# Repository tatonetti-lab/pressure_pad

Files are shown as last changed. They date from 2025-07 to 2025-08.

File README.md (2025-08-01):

# Pressure Sensor Pad for Real-Time Ulcer Detection
A smart pressure-sensing pad for early detection of pressure ulcers.

## 📖 Table of Contents
- [🔬 Project Overview](#-project-overview)
  - [Motivation](#motivation)
- [🛠 Hardware](#-hardware)
  - [Core Components](#core-components)
  - [Circuit Summary](#circuit-summary)
- [💻 Software \& Interface](#-software--interface)
  - [Arduino Firmware](#arduino-firmware)
  - [User Interface](#user-interface)
- [🧪 Testing \& Usage](#-testing--usage)
  - [Power Supply](#power-supply)
  - [Firmware Upload](#firmware-upload)
  - [Hardware Guide](#hardware-guide)
  - [Software Guide](#software-guide)
- [📊 Current Results](#-current-results)
- [⚠️ Current Limitations](#️-current-limitations)
- [🔮 Roadmap](#-roadmap)
- [👷 Troubleshooting Guide](#-troubleshooting-guide)
- [🧱 File Structure](#-file-structure)
- [✍️ Authors](#️-authors)

## 🔬 Project Overview
This project is a custom-built pressure sensor pad designed to detect and monitor pressure distribution in surgical and ICU settings. The goal is to identify high-risk regions for pressure ulcers in real time, aiding in preventative care for hospitalized patients.

### Motivation
Pressure ulcers are a major complication for bedridden or post-surgical patients. This device aims to reduce incidence by:
- Continuously monitoring pressure points beneath a patient
- Alerting clinicians to prolonged or high-risk pressure areas
- Improving quality of care, particularly in oncology and ICU units
>For a more in-depth analysis, go to [`/Docs/Pressure Pad Presentation.pdf`](https://github.com/tatonetti-lab/pressure_pad/blob/main/Docs/Pressure%20Pad%20Presentation.pdf)

## 🛠 Hardware

### Core Components
- **Microcontroller:** `Arduino GIGA R1 WiFi`
- **Sensor Matrix:** 23 x 32 grid using `Velostat` (a piezoresistive plastic that changes resistance under pressure)
- **Switching Logic:** `ADG728` I2C analog switches for matrix scanning
- **PCB:** Custom `KiCad` board with routed traces for all sensor inputs
- **Display:** `Arduino GIGA Display Shield` for on-device heatmap visualization

### Circuit Summary
- One row and one column are selected via ADG728s
- Voltage from each cell is read via the Arduino ADC
- Pressure intensity is inferred from voltage level
- Repeats rapidly across entire matrix to produce a live heatmap
>Circuit design allows scanning one row and one column at a time to measure pressure at each intersection.

## 💻 Software & Interface

### Arduino Firmware
- Collects analog pressure data from the sensor matrix
- Controls ADG728s via I2C to select matrix zones
- Sends data to GIGA Display for visualization

### User Interface
- Built in `SquareLine Studio`
- Features:
  - Home Screen
  - Live zone overview
  - Full pressure grid view
  - Future: historic trends + movement alerts

## 🧪 Testing & Usage

### Power Supply
- Power via USB-C or external 5V line

### Firmware Upload
1. Connect `Arduino GIGA R1 WiFi` via USB
2. Download the `PressurePadApp.zip`
3. Upload `PressurePadApp.ino` sketch using [**`Arduino IDE`**](https://www.arduino.cc/en/software/)

>Necessary libraries: `Arduino_GigaDisplayTouch`, `Arduino_GigaDisplay_GFX`, and `lvgl` **(v8.3.11)**.

### Hardware Guide
1. Insert the `Arduino GIGA Display Shield` into `Arduino GIGA R1`
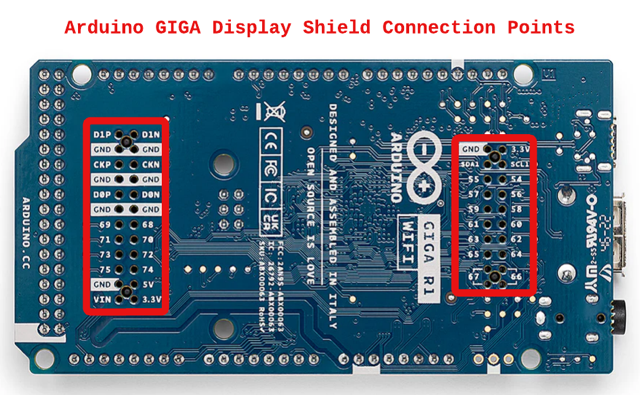
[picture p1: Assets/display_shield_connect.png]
display shield connect
   
2. Insert the `Arduino GIGA R1 WiFi + Display` into the PCB (female headers facing down)
   
3. Position the `pressure pad` so that the connection points are at the bottom right (`red` side facing up)
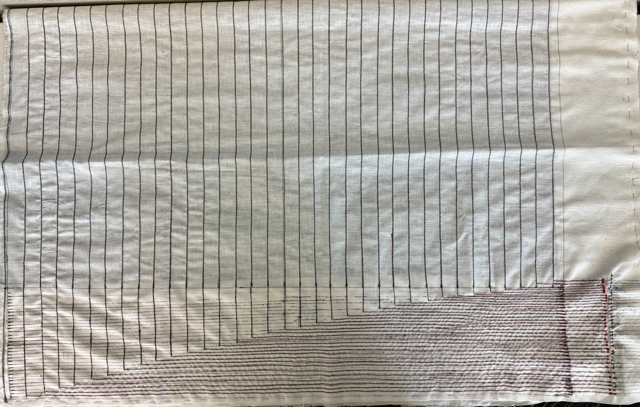
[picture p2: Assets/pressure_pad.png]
pressure pad
   
4. Wire pad to PCB:
   - **Red leads** → `DEMULTIPLEXER OUTPUTS` (vertical header, right)
   - **Blue leads** → `MULTIPLEXER INPUTS` (horizontal header, bottom)
5. Power the board

### Software Guide
>Once the system is powered on and the display shield is connected, the UI will launch automatically.

**Main Screens:**
- **`Home Page:`** Displays system status and navigation buttons to access `Live Data Overview` and `Historic Data` pages
- **`Live Data Overview:`** Displays 12 large, tappable buttons, each corresponding to a zone of the pressure pad
  - Each button changes color in real time based on average pressure in that region
  - Tap a button to enter that zone’s detailed heatmap
- **`Live Data:`** Shows an 8×8 heatmap of the selected zone from the pad
  - Color-coded for quick identification of high-pressure points
  - Updated continuously based on sensor readings
- **`Historic Data (Under Development):`** Will display trends in pressure over time and trigger alerts for high-risk zones

**Navigation:**
- Touchscreen is fully interactive (capacitive touch)
- Use on-screen buttons to switch between screens
- Tap return icons to go back to previous pages

**Interpreting the Heatmap:**
- Axis orientation matches the physical pad as connected to the PCB:
  - X-axis runs **right to left**
  - Y-axis runs **bottom to top**
- Colors represent pressure levels:
  - 🔴 Red = high pressure (risk of ulcers)
  - 🟣 Purple = moderate
  - 🔵 Blue = minimal or no pressure
- Live updates occur at ~20–50ms per cell

## 📊 Current Results
- All cells return live analog values
- Pressure heatmap successfully displayed in real time
- PCB assembled and functioning as intended
- Future test deployment planned at Cedars-Sinai surgical suite

## ⚠️ Current Limitations

- Top sensor row (y = 24) currently shows noise due to physical layout constraints
- Calibration may vary with sensor wear
- Data is real-time only; historic pressure history not yet stored
- No wireless/cloud connectivity yet
- Must be handled carefully to avoid flex damage in Velostat

## 🔮 Roadmap

| Milestone                     | Status     |
|------------------------------|------------|
| Initial prototype            | ✅ Complete |
| PCB design and assembly      | ✅ Complete |
| Real-time display            | ✅ Complete |
| Historic data + alert logic  | 🔄 In progress |
| Clinical suite testing       | 🔜 Planned |

## 👷 Troubleshooting Guide

| Problem                                      | Possible Cause                                             | Solution                                                                 |
|----------------------------------------------|------------------------------------------------------------|--------------------------------------------------------------------------|
| Heatmap shows no data                        | Arduino not powered or not connected properly              | Check USB/5V supply and USB cable connection                            |
| Only partial pad is active                   | Incorrect multiplexer/demultiplexer wiring                 | Verify wiring between PCB and pad (red = demux, blue = mux)             |
| Data appears inverted or mirrored            | Pad is oriented incorrectly                                | Rotate the pad so the connection points are at the bottom right         |
| Zones not updating in UI                     | I2C communication issue or faulty ADG728                   | Check I2C addresses and power to switches                               |
| Arduino not recognized in IDE                | Wrong port or missing driver                               | Ensure correct port is selected and install board package in Arduino IDE |
| No image shown on display                    | Display shield not connected correctly                     | Reseat the display shield onto Arduino GIGA pins                        |
| Colors frozen on screen                      | Loop not running or memory issue                           | Reset Arduino, monitor serial for errors                                |
| Boot0 light flashing red after upload        | Invalid code upload or memory overflow                     | Double-click the RST button on top right of the Arduino (back-side) & reupload code |
| Solder joints not connecting (Arduino back)  | No through-holes to allow solder to bridge to PCB          | Use angled headers, conductive epoxy, or jumper wires to reroute traces |

## 🧱 File Structure
<pre>
pressure_pad/
├── PressurePadApp/             # Arduino firmware and UI code
│   ├── PressurePadApp.ino
│   ├── ui_*.c / .h             # UI pages and assets
│   └── CMakeLists.txt
├── KiCad/                      # PCB schematic and layout files
│   └── pressure_pad.kicad_*
├── Assets/                     # Images for documentation
│   └── *.png
├── Docs/                       # Slides, references, design notes
│   └── *.pdf
├── DenoisingAutoencoder_OLD/   # Legacy Python scripts and ML notebooks
│   ├── no_touch_set/
│   ├── 6x6/
│   ├── *.ipynb
│   └── pressure_pad_study.db
└── .vscode/                    # VSCode config (not necessary for implementation)
</pre>

## ✍️ Authors

- [@AlexAhitov](https://github.com/AlexAhitov)

[**Back to the top**](#pressure-sensor-pad-for-real-time-ulcer-detection)

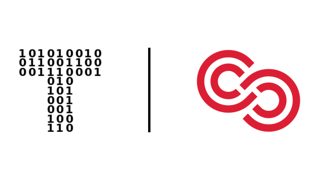
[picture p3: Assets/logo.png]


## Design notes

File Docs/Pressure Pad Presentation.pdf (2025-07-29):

# Real-Time Pressure Sensor

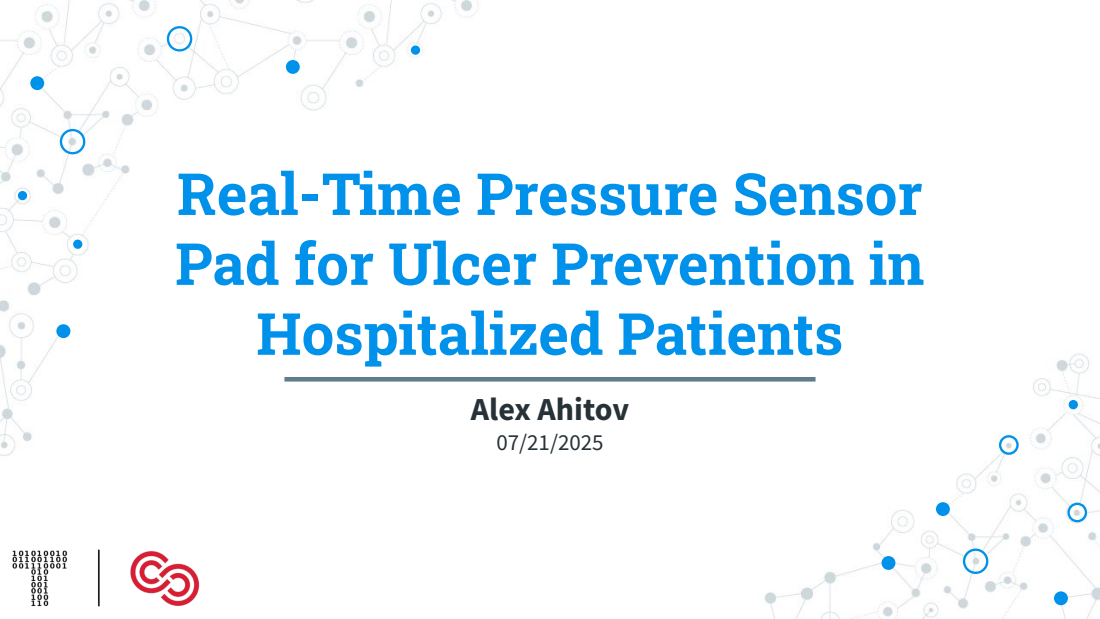
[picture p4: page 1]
Alex Ahitov

Pad for Ulcer Prevention in
Hospitalized Patients

### Motivation / Aim

Clinical Problem:
◎ Ulcers and bedsores are common in ICU & surgical patients. Impact:
◎ Increase infections, hospital stays, and costs.
Project Aim:
◎ Real-time pressure monitoring to prevent ulcers by guiding

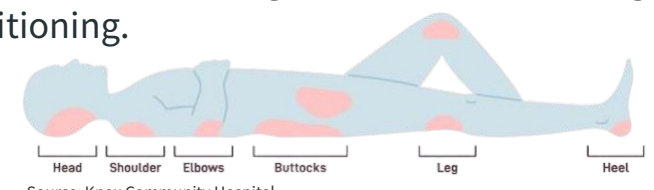
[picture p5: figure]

timely repositioning.

Source: Knox Community Hospital (https://www.kch.org/pressure-ulcers) | 2

### Background

Current Standard of Care
◎ Manual turning schedules or subjective monitoring.
Limitations:
◎ No continuous, objective feedback for nurses or physicians.
Our Approach:
◎ A real-time pad that provides actionable data to healthcare professionals.

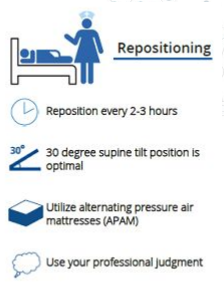
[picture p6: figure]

3

Source: Wound Care Surgeons (https://www.woundcaresurgeons.org/blogs/all-you-need-to-know-about-pressure-ulcers)

### Methods: System Development Overview

◎ Pipeline:

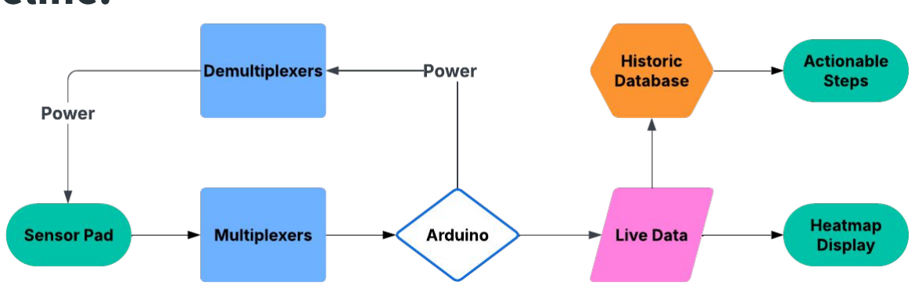
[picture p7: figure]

◎ Key Design Goals: High resolution, low noise, scalable to full-body pad.

4

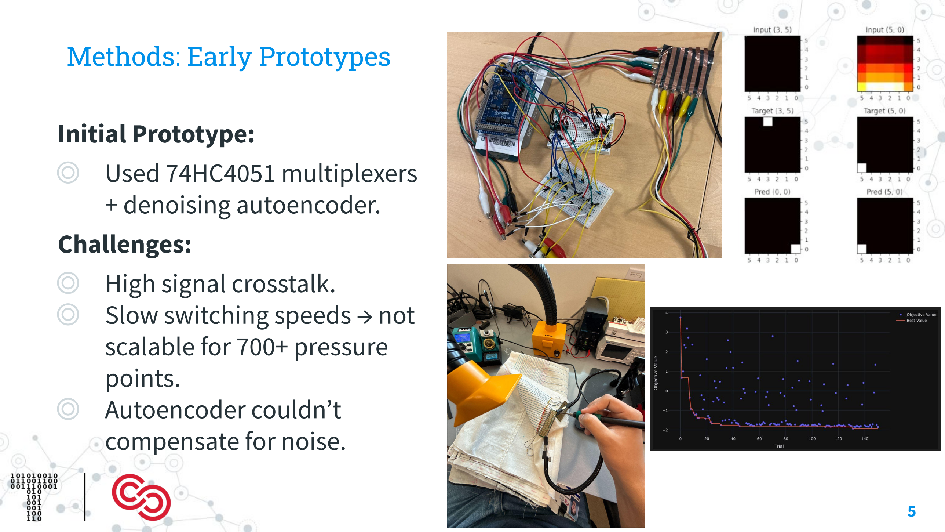
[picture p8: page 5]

### Methods: Early Prototypes

Initial Prototype: ◎ Used 74HC4051 multiplexers

+ denoising autoencoder.
Challenges: ◎ High signal crosstalk. ◎ Slow switching speeds → not

scalable for 700+ pressure points.
◎ Autoencoder couldnʼt
compensate for noise.

5

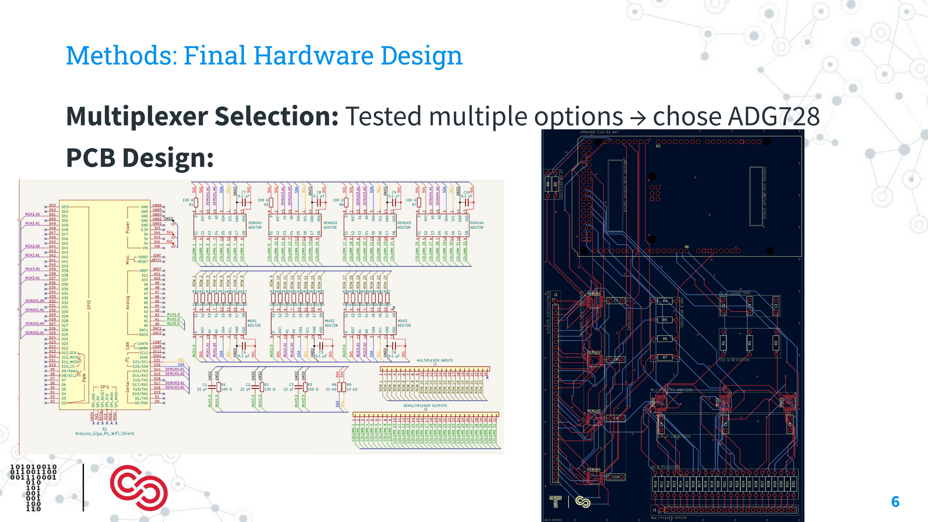
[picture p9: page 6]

### Methods: Final Hardware Design

Multiplexer Selection: Tested multiple options → chose ADG728 PCB Design:

6

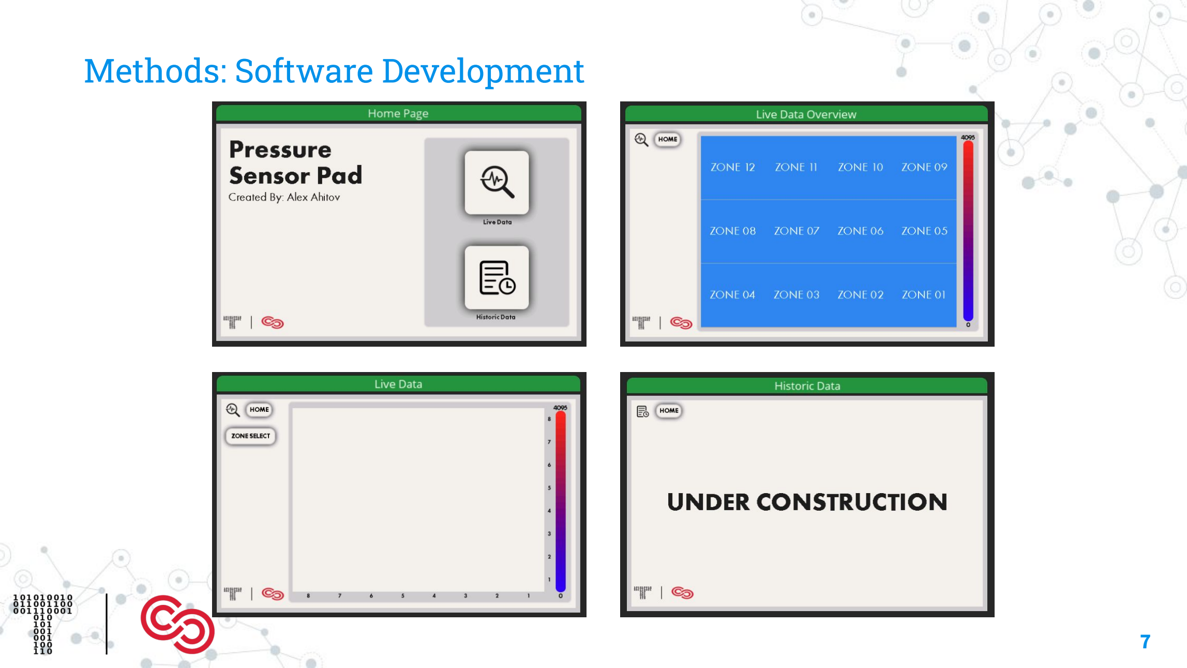
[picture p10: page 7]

### Methods: Software Development

7

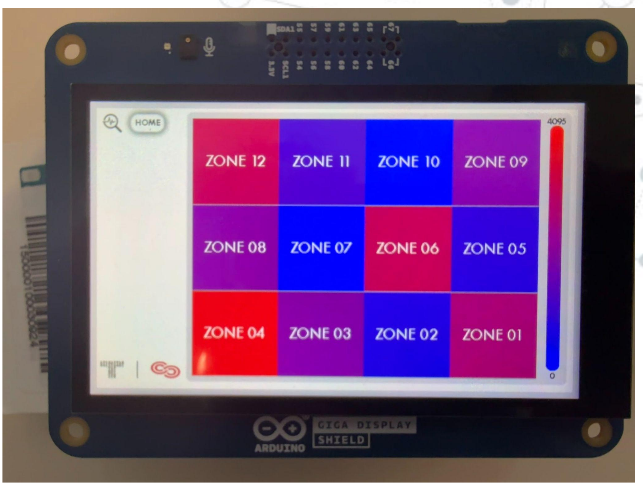
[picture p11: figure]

### Current Results

What Works Now: ◎ Real-time data

visualization for all zones. ◎ Zone recoloring reflects relative pressure risk.
Current Status: ◎ PCB boards arriving today

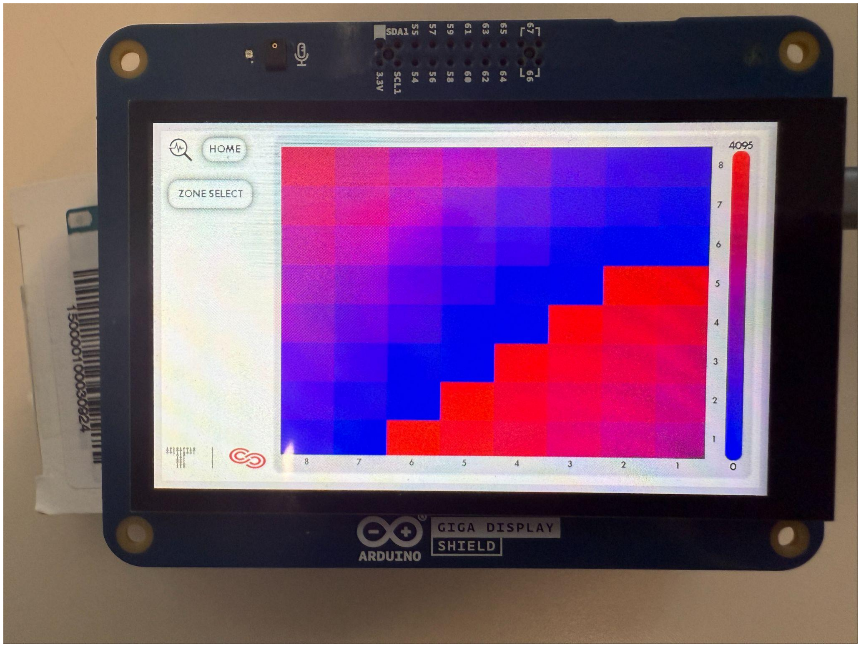
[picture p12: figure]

→ no live demo yet.

8

### Future Steps

Software:
◎ Add historic data logging to show how long high
pressure persists.
Clinical Testing:
◎ Test out pressure pad in a Cedars-Sinai surgical
suite.

9

Big Vision:
◎ Automated repositioning
alerts for nurses → reduce ulcer incidence.

### Conclusion

✓ Built a working real-time pressure-sensing pad with live heatmap visualization.
✓ Hardware and software ready for clinical testing; PCB arriving today.
✓ Potential to reduce ulcer incidence by providing actionable repositioning data for ICU and surgical patients.

10

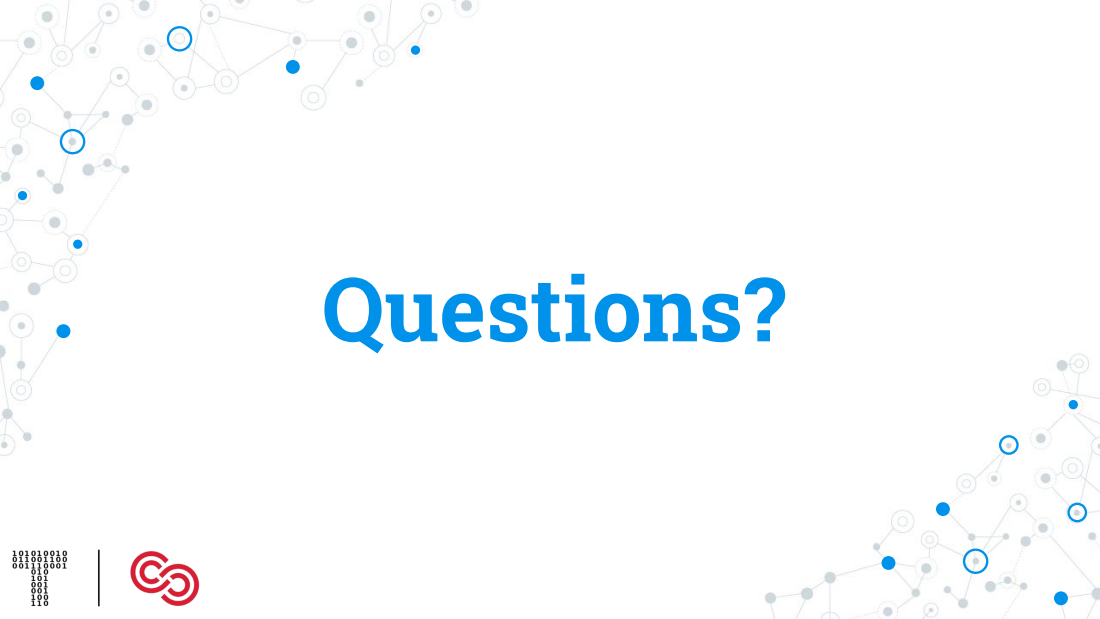
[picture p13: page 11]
Questions?

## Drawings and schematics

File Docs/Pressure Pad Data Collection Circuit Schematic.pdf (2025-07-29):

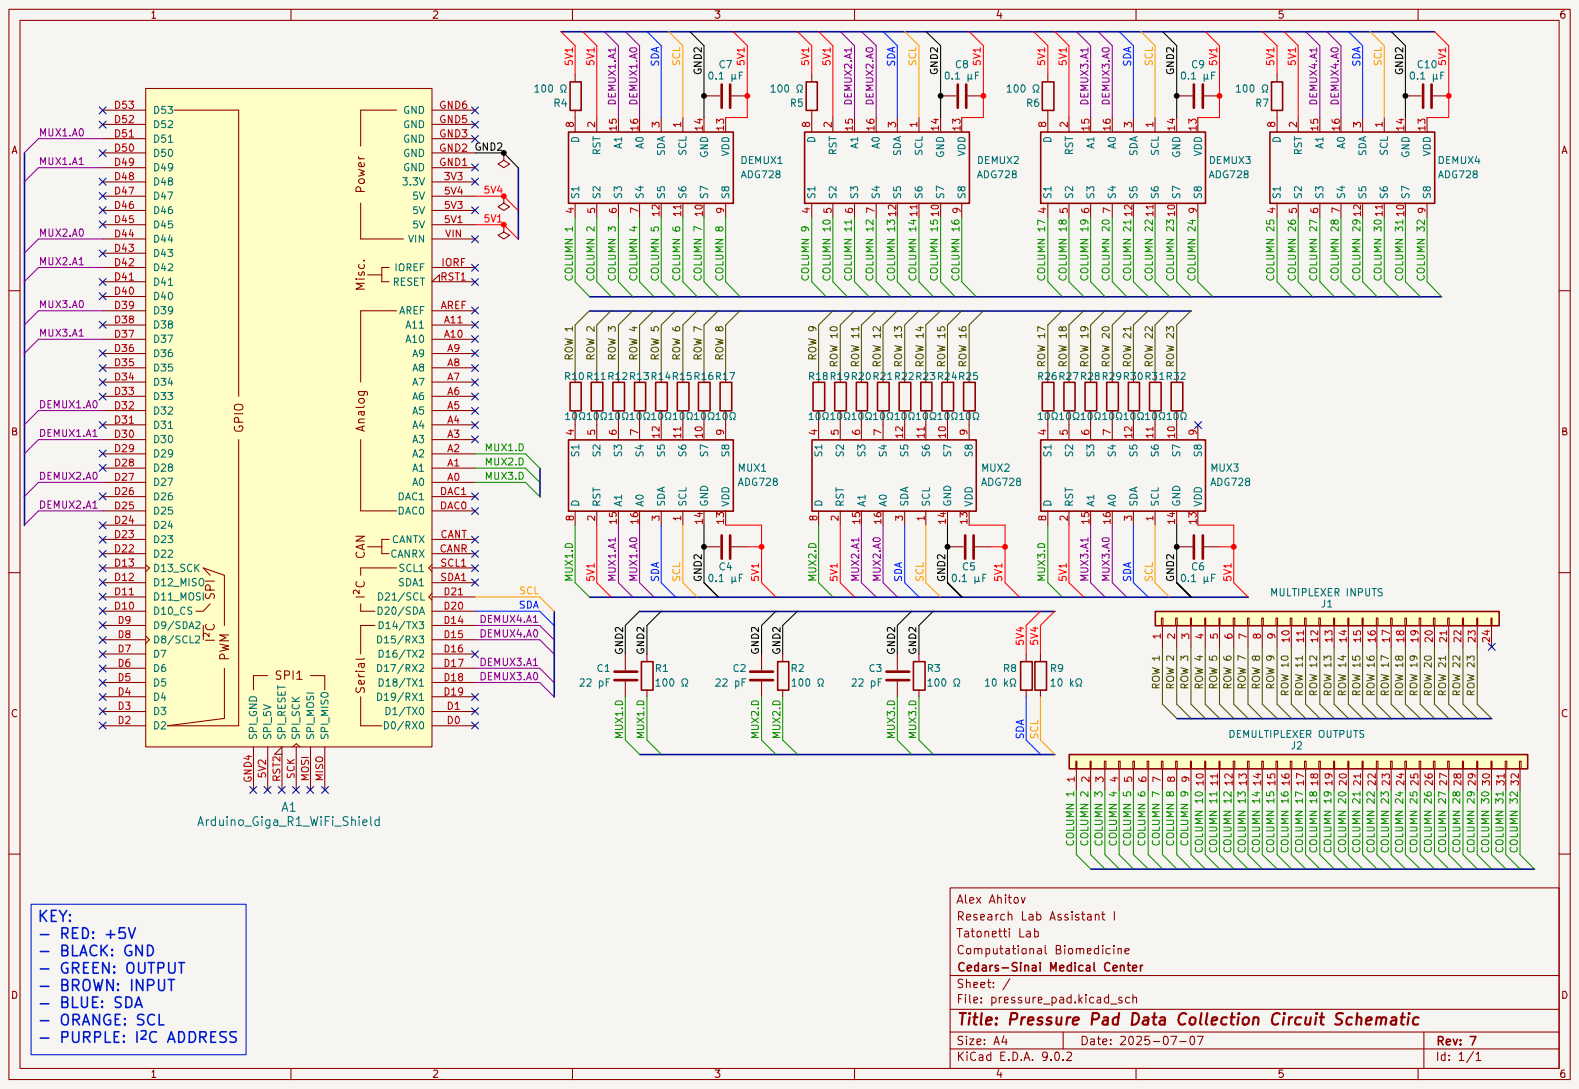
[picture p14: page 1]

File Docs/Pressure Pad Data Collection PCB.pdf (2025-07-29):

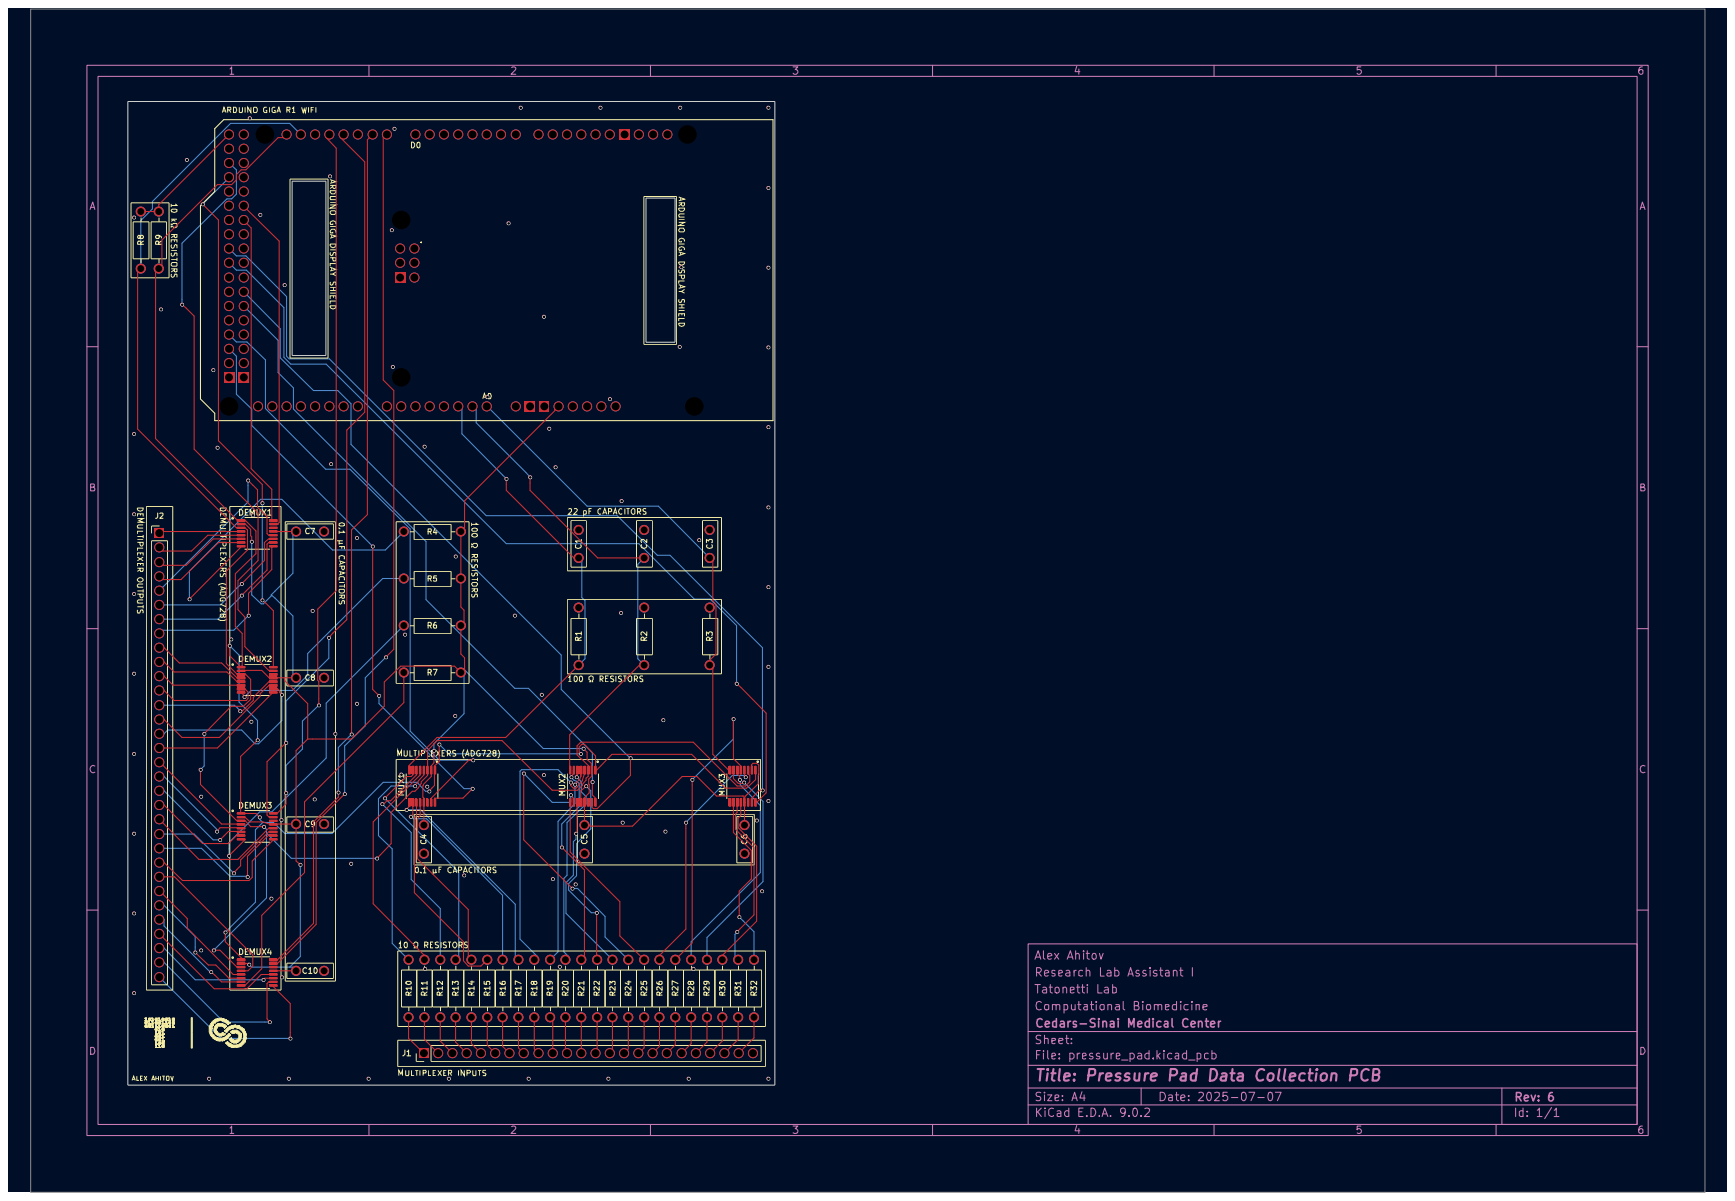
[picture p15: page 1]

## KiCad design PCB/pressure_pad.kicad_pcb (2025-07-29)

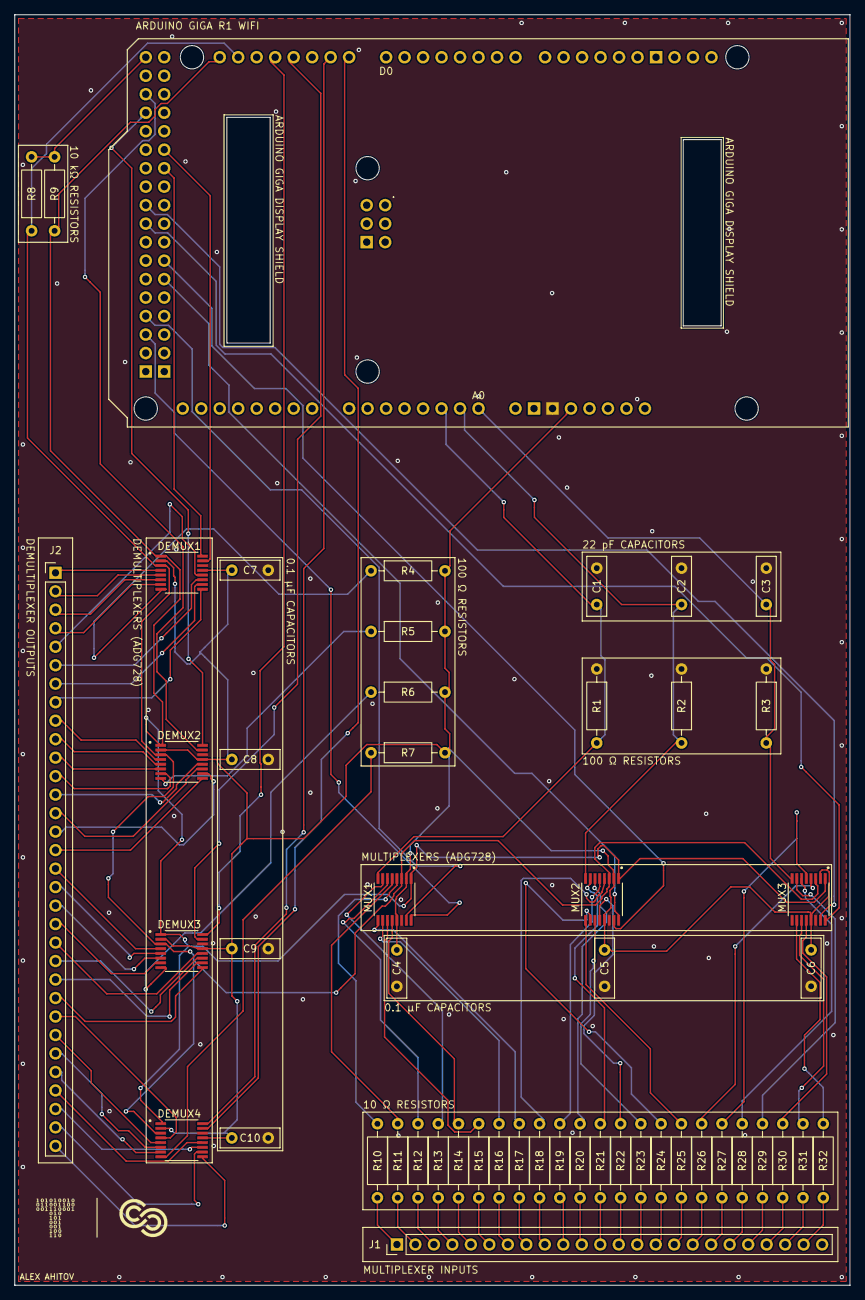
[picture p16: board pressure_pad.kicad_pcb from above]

Board: 2 copper layers, 114.8 x 174.6 mm, 52 parts (1 on the bottom side), 104 nets.

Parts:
A1: Arduino_Giga_R1_WiFi_Shield
C1, C2, C3: 22 pF; C_Disc_D8.0mm_W2.5mm_P5.00mm
C4, C5, C6, C7, C8, C9, C10: 0.1 µF; C_Disc_D8.0mm_W2.5mm_P5.00mm
DEMUX1, DEMUX2, DEMUX3, DEMUX4: ADG728; SOP65P640X120-16N
J1: MULTIPLEXER INPUTS; PinHeader_1x24_P2.54mm_Vertical
J2: DEMULTIPLEXER OUTPUTS; PinHeader_1x32_P2.54mm_Vertical
MUX1, MUX2, MUX3: ADG728; SOP65P640X120-16N
R1, R2, R3, R4, R5, R6, R7: 100 Ω; R_Axial_DIN0207_L6.3mm_D2.5mm_P10.16mm_Horizontal
R8, R9: 10 kΩ; R_Axial_DIN0207_L6.3mm_D2.5mm_P10.16mm_Horizontal
R10, R11, R12, R13, R14, R15, R16, R17, R18, R19, R20, R21, R22, R23, R24, R25, R26, R27, R28, R29, R30, R31, R32: 10Ω; R_Axial_DIN0207_L6.3mm_D2.5mm_P10.16mm_Horizontal

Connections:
/5V1: A1.5V1 (5V), C4.2, C5.2, C6.2, C7.2, C8.2, C9.2, C10.2, DEMUX1.2 (RST), DEMUX1.13 (VDD), DEMUX2.2 (RST), DEMUX2.13 (VDD), DEMUX3.2 (RST), DEMUX3.13 (VDD), DEMUX4.2 (RST), DEMUX4.13 (VDD), MUX1.2 (RST), MUX1.13 (VDD), MUX2.2 (RST), MUX2.13 (VDD), MUX3.2 (RST), MUX3.13 (VDD), R4.2, R5.2, R6.2, R7.2
/5V4: A1.5V4 (5V), R8.2, R9.2
/COLUMN 1: DEMUX1.4 (S1), J2.1
/COLUMN 2: DEMUX1.5 (S2), J2.2
/COLUMN 3: DEMUX1.6 (S3), J2.3
/COLUMN 4: DEMUX1.7 (S4), J2.4
/COLUMN 5: DEMUX1.12 (S5), J2.5
/COLUMN 6: DEMUX1.11 (S6), J2.6
/COLUMN 7: DEMUX1.10 (S7), J2.7
/COLUMN 8: DEMUX1.9 (S8), J2.8
/COLUMN 9: DEMUX2.4 (S1), J2.9
/COLUMN 10: DEMUX2.5 (S2), J2.10
/COLUMN 11: DEMUX2.6 (S3), J2.11
/COLUMN 12: DEMUX2.7 (S4), J2.12
/COLUMN 13: DEMUX2.12 (S5), J2.13
/COLUMN 14: DEMUX2.11 (S6), J2.14
/COLUMN 15: DEMUX2.10 (S7), J2.15
/COLUMN 16: DEMUX2.9 (S8), J2.16
/COLUMN 17: DEMUX3.4 (S1), J2.17
/COLUMN 18: DEMUX3.5 (S2), J2.18
/COLUMN 19: DEMUX3.6 (S3), J2.19
/COLUMN 20: DEMUX3.7 (S4), J2.20
/COLUMN 21: DEMUX3.12 (S5), J2.21
/COLUMN 22: DEMUX3.11 (S6), J2.22
/COLUMN 23: DEMUX3.10 (S7), J2.23
/COLUMN 24: DEMUX3.9 (S8), J2.24
/COLUMN 25: DEMUX4.4 (S1), J2.25
/COLUMN 26: DEMUX4.5 (S2), J2.26
/COLUMN 27: DEMUX4.6 (S3), J2.27
/COLUMN 28: DEMUX4.7 (S4), J2.28
/COLUMN 29: DEMUX4.12 (S5), J2.29
/COLUMN 30: DEMUX4.11 (S6), J2.30
/COLUMN 31: DEMUX4.10 (S7), J2.31
/COLUMN 32: DEMUX4.9 (S8), J2.32
/DEMUX1.A0: A1.D32, DEMUX1.16 (A0)
/DEMUX1.A1: A1.D30, DEMUX1.15 (A1)
/DEMUX2.A0: A1.D27, DEMUX2.16 (A0)
/DEMUX2.A1: A1.D25, DEMUX2.15 (A1)
/DEMUX3.A0: A1.D18 (D18/TX1), DEMUX3.16 (A0)
/DEMUX3.A1: A1.D17 (D17/RX2), DEMUX3.15 (A1)
/DEMUX4.A0: A1.D15 (D15/RX3), DEMUX4.16 (A0)
/DEMUX4.A1: A1.D14 (D14/TX3), DEMUX4.15 (A1)
/GND2: A1.GND2 (GND), C1.1, C2.1, C3.1, C4.1, C5.1, C6.1, C7.1, C8.1, C9.1, C10.1, DEMUX1.14 (GND), DEMUX2.14 (GND), DEMUX3.14 (GND), DEMUX4.14 (GND), MUX1.14 (GND), MUX2.14 (GND), MUX3.14 (GND), R1.1, R2.1, R3.1
/MUX1.A0: A1.D51, MUX1.16 (A0)
/MUX1.A1: A1.D49, MUX1.15 (A1)
/MUX1.D: A1.A2, C1.2, MUX1.8 (D), R1.2
/MUX2.A0: A1.D44, MUX2.16 (A0)
/MUX2.A1: A1.D42, MUX2.15 (A1)
/MUX2.D: A1.A1, C2.2, MUX2.8 (D), R2.2
/MUX3.A0: A1.D39, MUX3.16 (A0)
/MUX3.A1: A1.D37, MUX3.15 (A1)
/MUX3.D: A1.A0, C3.2, MUX3.8 (D), R3.2
/ROW 1: J1.1, R10.1
/ROW 2: J1.2, R11.1
/ROW 3: J1.3, R12.1
/ROW 4: J1.4, R13.1
/ROW 5: J1.5, R14.1
/ROW 6: J1.6, R15.1
/ROW 7: J1.7, R16.1
/ROW 8: J1.8, R17.1
/ROW 9: J1.9, R18.1
/ROW 10: J1.10, R19.1
/ROW 11: J1.11, R20.1
/ROW 12: J1.12, R21.1
/ROW 13: J1.13, R22.1
/ROW 14: J1.14, R23.1
/ROW 15: J1.15, R24.1
/ROW 16: J1.16, R25.1
/ROW 17: J1.17, R26.1
/ROW 18: J1.18, R27.1
/ROW 19: J1.19, R28.1
/ROW 20: J1.20, R29.1
/ROW 21: J1.21, R30.1
/ROW 22: J1.22, R31.1
/ROW 23: J1.23, R32.1
/SCL: A1.D21 (D21/SCL), DEMUX1.1 (SCL), DEMUX2.1 (SCL), DEMUX3.1 (SCL), DEMUX4.1 (SCL), MUX1.1 (SCL), MUX2.1 (SCL), MUX3.1 (SCL), R9.1
/SDA: A1.D20 (D20/SDA), DEMUX1.3 (SDA), DEMUX2.3 (SDA), DEMUX3.3 (SDA), DEMUX4.3 (SDA), MUX1.3 (SDA), MUX2.3 (SDA), MUX3.3 (SDA), R8.1
unnamed: DEMUX1.8 (D), R4.1
unnamed: DEMUX2.8 (D), R5.1
unnamed: DEMUX3.8 (D), R6.1
unnamed: DEMUX4.8 (D), R7.1
unnamed: MUX1.4 (S1), R10.2
unnamed: MUX1.5 (S2), R11.2
unnamed: MUX1.6 (S3), R12.2
unnamed: MUX1.7 (S4), R13.2
unnamed: MUX1.12 (S5), R14.2
unnamed: MUX1.11 (S6), R15.2
unnamed: MUX1.10 (S7), R16.2
unnamed: MUX1.9 (S8), R17.2
unnamed: MUX2.4 (S1), R18.2
unnamed: MUX2.5 (S2), R19.2
unnamed: MUX2.6 (S3), R20.2
unnamed: MUX2.7 (S4), R21.2
unnamed: MUX2.12 (S5), R22.2
unnamed: MUX2.11 (S6), R23.2
unnamed: MUX2.10 (S7), R24.2
unnamed: MUX2.9 (S8), R25.2
unnamed: MUX3.4 (S1), R26.2
unnamed: MUX3.5 (S2), R27.2
unnamed: MUX3.6 (S3), R28.2
unnamed: MUX3.7 (S4), R29.2
unnamed: MUX3.12 (S5), R30.2
unnamed: MUX3.11 (S6), R31.2
unnamed: MUX3.10 (S7), R32.2

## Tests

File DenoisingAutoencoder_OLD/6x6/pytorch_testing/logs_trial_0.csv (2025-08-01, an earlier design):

epoch | val_loss | external_accuracy
1 | 1.8629911526389744 | 0.26851851851851855
2 | 1.7584037055139956 | 0.3333333333333333
3 | 1.6759758368782376 | 0.35185185185185186
4 | 1.6523341417312623 | 0.35185185185185186
5 | 1.587321744794431 | 0.3611111111111111
6 | 1.550897961077483 | 0.3703703703703704
7 | 1.5298736976540608 | 0.3425925925925926
8 | 1.5280707320441371 | 0.3333333333333333
9 | 1.4955503982046376 | 0.3796296296296296
10 | 1.4566169624743255 | 0.39814814814814814
11 | 1.4527950022531593 | 0.35185185185185186
12 | 1.4035497973794522 | 0.3611111111111111
13 | 1.3629767412724703 | 0.3611111111111111
14 | 1.3925548467947089 | 0.3333333333333333
15 | 1.3524637245613595 | 0.3703703703703704
16 | 1.316436315101126 | 0.3611111111111111
17 | 1.3487726633963377 | 0.3148148148148148
18 | 1.3118423811767412 | 0.35185185185185186
19 | 1.2727985141069993 | 0.35185185185185186
20 | 1.348239022752513 | 0.3148148148148148
21 | 1.232020119998766 | 0.39814814814814814
22 | 1.2393186227135036 | 0.35185185185185186
23 | 1.3075932101063106 | 0.3611111111111111
24 | 1.236841883348382 | 0.3703703703703704
25 | 1.1912872923457105 | 0.3425925925925926
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

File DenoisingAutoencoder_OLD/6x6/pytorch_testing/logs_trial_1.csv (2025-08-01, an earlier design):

epoch | val_loss | external_accuracy
1 | 2.707818795894754 | 0.009259259259259259
2 | 2.261580726196026 | 0.08333333333333333
3 | 1.8223174502109658 | 0.07407407407407407
4 | 1.688858726928974 | 0.07407407407407407
5 | 1.641354160062198 | 0.1111111111111111
6 | 1.6027790677958522 | 0.13888888888888887
7 | 1.570735357958695 | 0.16666666666666666
8 | 1.5538865142855152 | 0.19444444444444442
9 | 1.536566067358543 | 0.23148148148148148
10 | 1.5168452858924866 | 0.2222222222222222
11 | 1.497836179774383 | 0.21296296296296294
12 | 1.4855848016410038 | 0.25
13 | 1.4803614739713997 | 0.26851851851851855
14 | 1.4615273516753624 | 0.25
15 | 1.4513367650837734 | 0.28703703703703703
16 | 1.4385455127420097 | 0.2777777777777778
17 | 1.431445446507684 | 0.3055555555555556
18 | 1.4253083159183633 | 0.3333333333333333
19 | 1.4135545317468972 | 0.324074074074074
20 | 1.4037932116409828 | 0.3333333333333333
21 | 1.404035981359153 | 0.3425925925925926
22 | 1.3907286812519204 | 0.3240740740740741
23 | 1.3814300082880875 | 0.34259259259259256
24 | 1.3734748630688107 | 0.3703703703703704
25 | 1.367964545200611 | 0.3611111111111111
26 | 1.3631311182318062 | 0.3796296296296296
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
